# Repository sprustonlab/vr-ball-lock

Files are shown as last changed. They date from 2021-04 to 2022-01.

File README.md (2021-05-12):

# vr-ball-lock

## Notes
Theres a very bright LED on the PCA9685 board. I couldnt remove it by desodering but the board seems to work fine after I just broke the LED with a plier.
## testing the arduino uno control
You can add a simple jumper cable between digital pin 11 and 12. This will cycle between on/off every second.

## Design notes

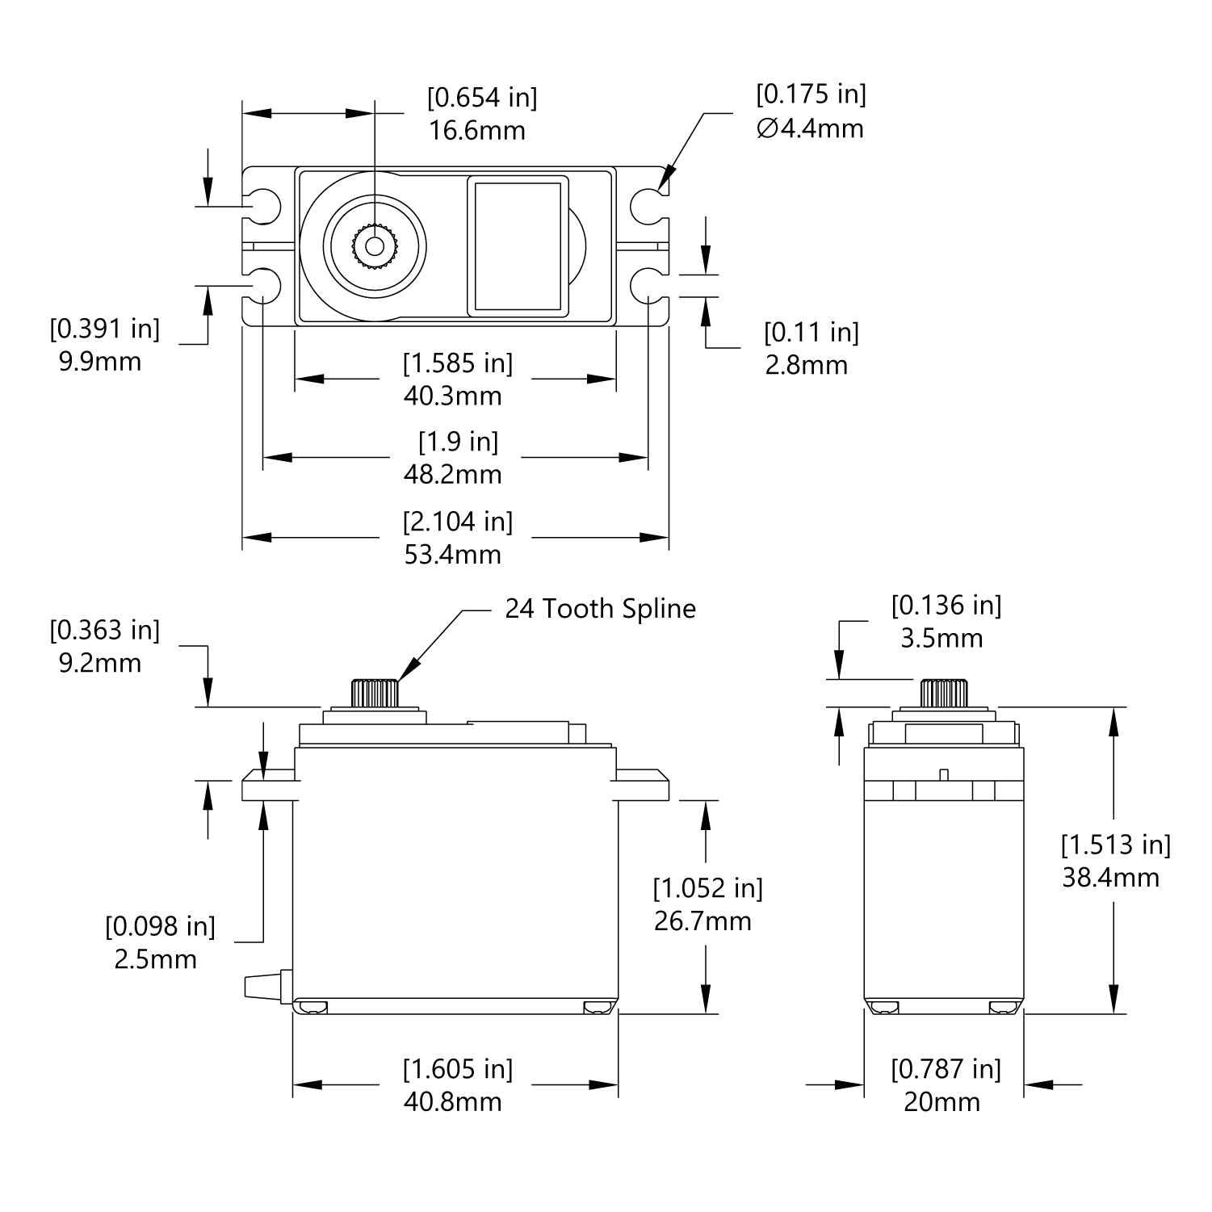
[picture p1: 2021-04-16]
Inventor Models/Parts/Hitec-HS-422-Schematic__34470.1591133086.png

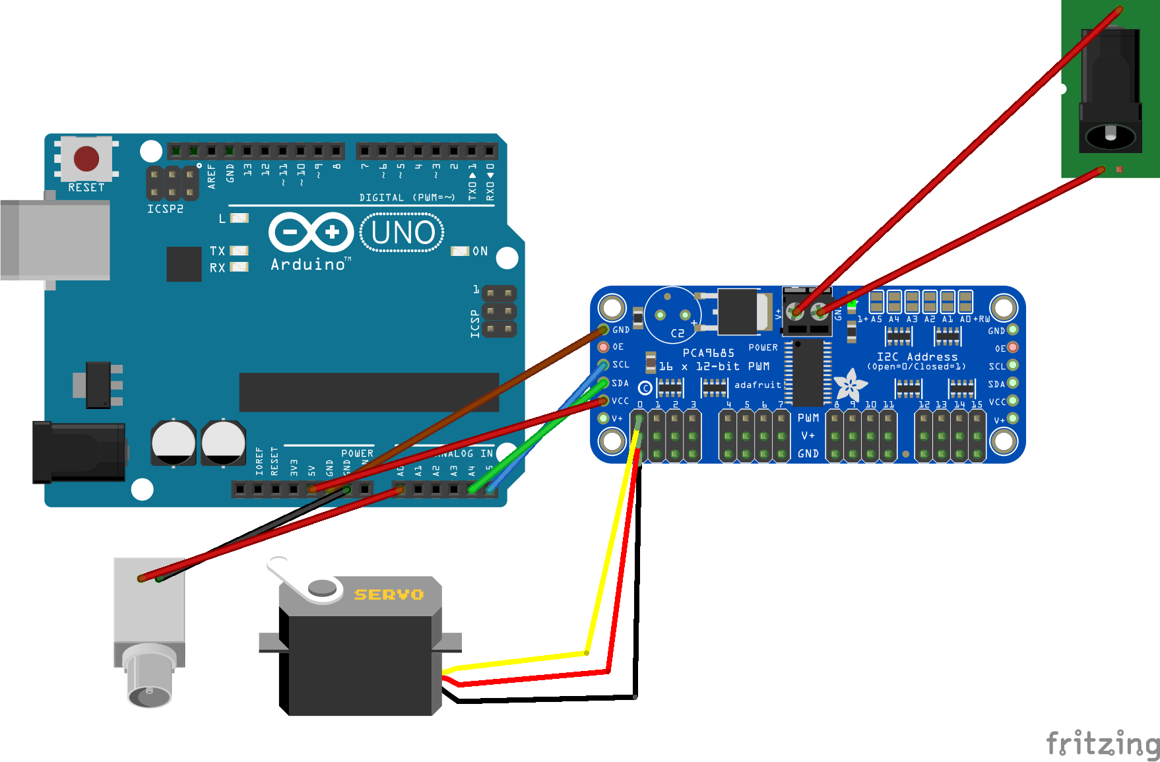
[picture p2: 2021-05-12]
electronics schematic/ball lock Schematic_bb.png

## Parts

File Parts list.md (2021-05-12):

# Main Components
* Servo: [HS-422 Deluxe Standard Servo | HITEC RCD USA](https://hitecrcd.com/products/servos/sport-servos/analog-sport-servos/hs-422/product)

* Servo Motor Driver PCA9685: [https://www.amazon.com/dp/B07Z8R2YB9](https://www.amazon.com/dp/B07Z8R2YB9) $13.99

* Arduino Uno: [https://www.amazon.com/dp/B008GRTSV6](https://www.amazon.com/dp/B008GRTSV6) $22.50

* Arduino Uno case: [https://www.amazon.com/dp/B01C8500L8](https://www.amazon.com/dp/B01C8500L8)$4.89

 * 5V 4A Power Supply Charger  DC 5.5mm x 2.1mm: [https://www.amazon.com/dp/B08VWVLBWF](https://www.amazon.com/dp/B08VWVLBWF) $11.99

# Conectors

* Female Red Black DC Power Pigtail Female Cable Lead Plug 10in 2.1x5.5mm [https://www.amazon.com/dp/B01N5JHFC0](https://www.amazon.com/dp/B01N5JHFC0) $8.59

* 1x Female Jack to AV 2 Screw Terminal Connector [https://www.amazon.com/dp/B07TT14RGF](https://www.amazon.com/dp/B07TT14RGF) $8.99 

# Cables
 * 1x 25 feet bnc cable [https://www.amazon.com/dp/B07R567S3J](https://www.amazon.com/dp/B07R567S3J) $31.99

 * 5.5mm x 2.1mm Extension Cord (5m), [https://www.amazon.com/dp/B08GZ8JP87](https://www.amazon.com/dp/B08GZ8JP87) $8.99

 * 900mm Servo Extension: [https://www.amazon.com/dp/B074SZXXGM](https://www.amazon.com/dp/B074SZXXGM) $10.90

 * Jumper wires: [https://www.amazon.com/dp/B07GD2BWPY](https://www.amazon.com/dp/B07GD2BWPY) $5.99

 # Power cable

## Cable fabrication (Steve)
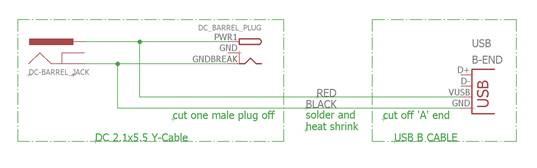
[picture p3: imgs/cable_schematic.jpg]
Schematic cable
 
 ## Off the shelf solution
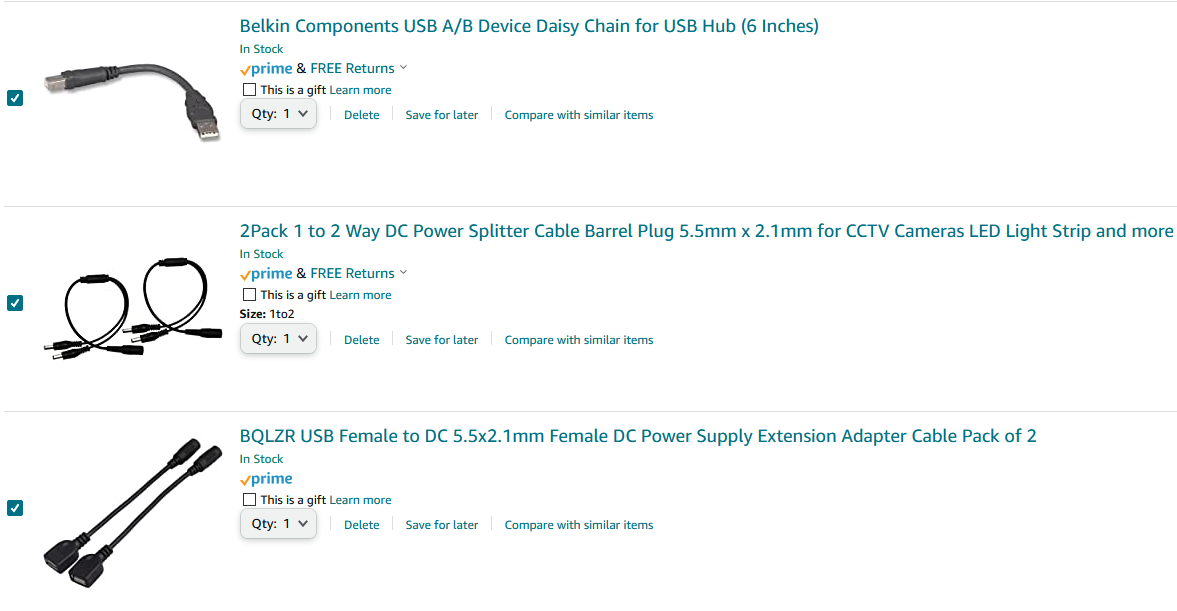
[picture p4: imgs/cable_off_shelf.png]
off the shelf cables


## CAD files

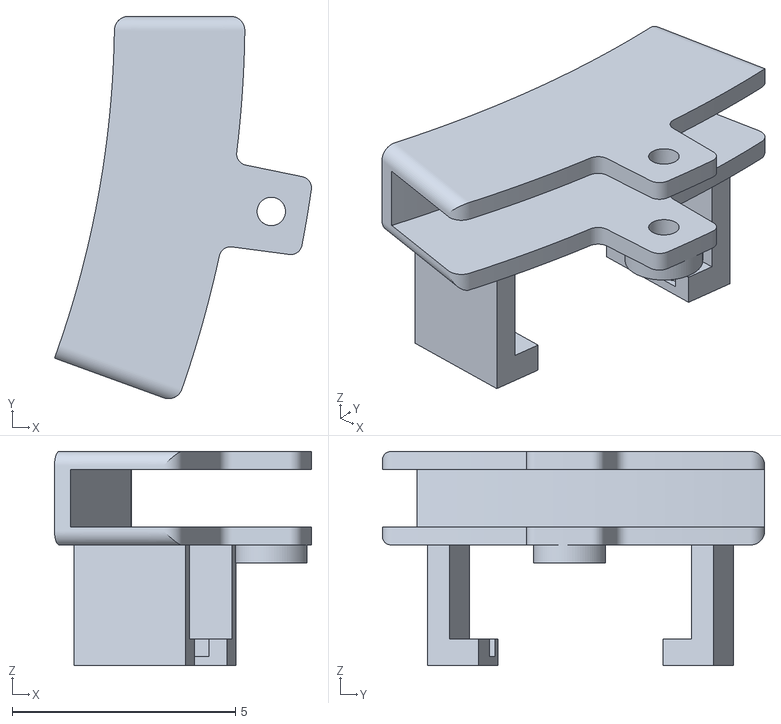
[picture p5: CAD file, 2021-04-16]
3d prints/Holder/Frame Holder.stl
5.75 x 8.56 x 4.80

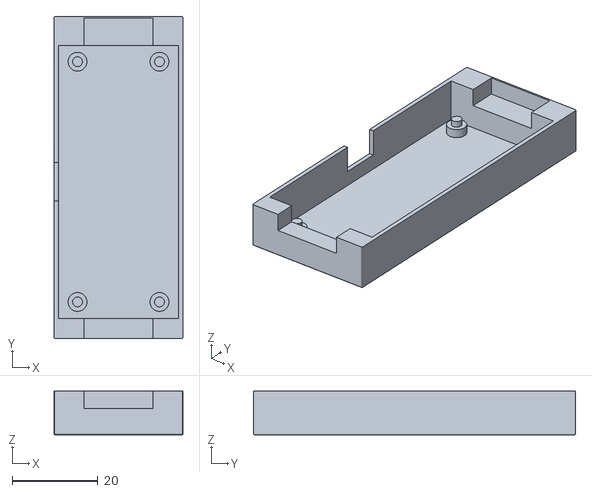
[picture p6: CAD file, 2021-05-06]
3d prints/PCA9685 case/Bottom_generic_v4.stl
30.0 x 75.0 x 10.2

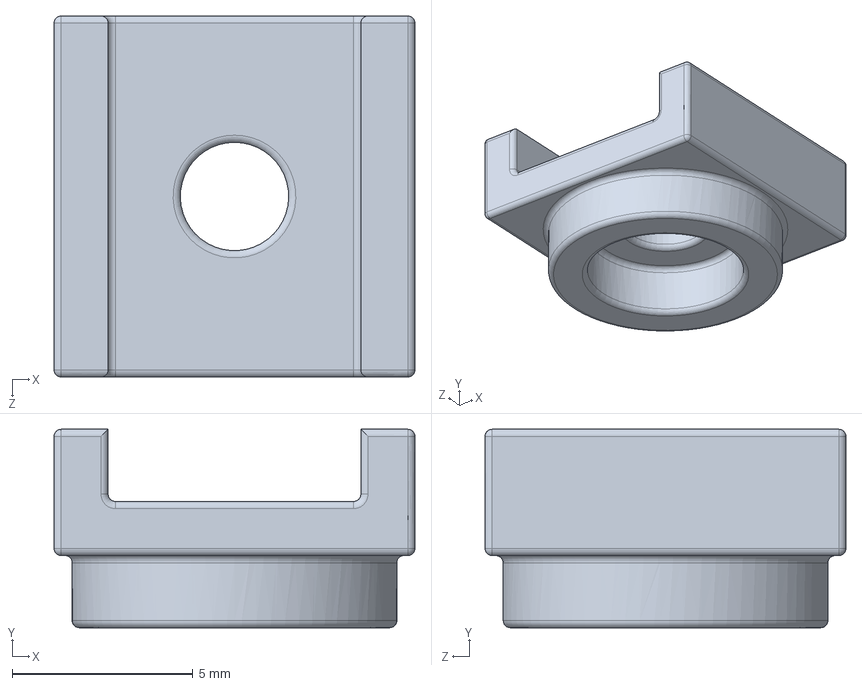
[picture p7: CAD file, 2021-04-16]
Inventor Models/Parts/base de riel.SLDPRT
10.0 x 5.50 x 10.0 mm

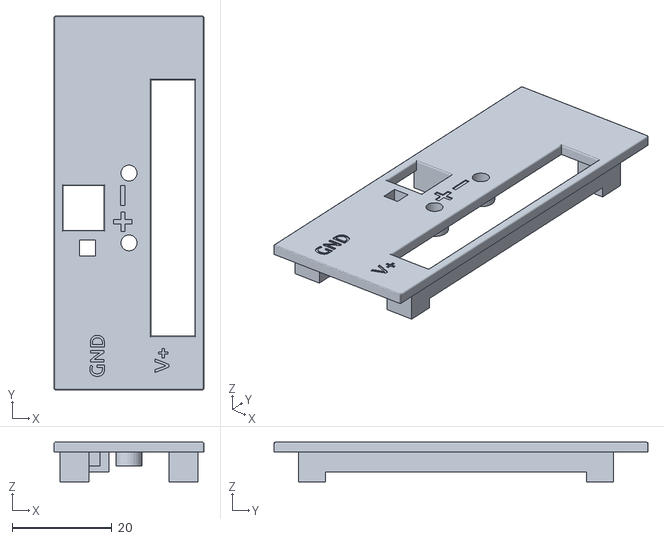
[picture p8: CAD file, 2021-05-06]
3d prints/PCA9685 case/Top_v4_ft_China.stl
30.0 x 75.0 x 8.00

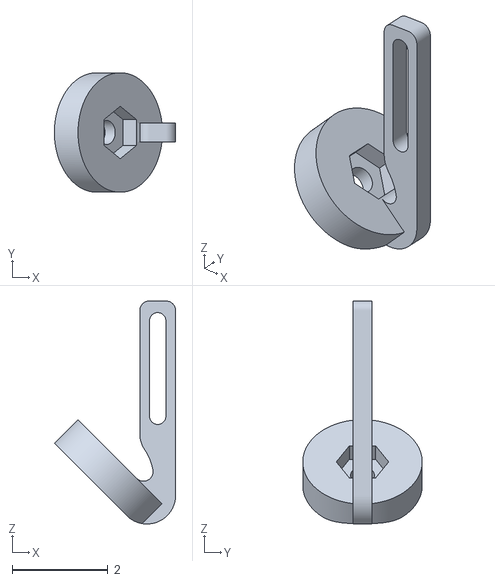
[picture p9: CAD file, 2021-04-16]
Inventor Models/Parts/arm.obj
2.54 x 2.50 x 4.67

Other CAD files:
Inventor Models/Parts/16 inch ball treadmill frame v2.ipt
Inventor Models/Parts/Frame Holder.ipt
Inventor Models/Parts/arm.ipt
Inventor Models/Parts/base de riel.ipt
Inventor Models/Parts/hs-422_sws.SLDPRT
Inventor Models/Parts/hs-422_sws.ipt
Inventor Models/Parts/servo connector.ipt
Inventor Models/Stop System Assembly.iam

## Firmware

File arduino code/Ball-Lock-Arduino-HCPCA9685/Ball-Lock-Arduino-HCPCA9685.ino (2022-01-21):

/*

  To use the PCA9685 module connect it to your Arduino as follows:

  PCA9685...........Uno/Nano
  GND...............GND
  OE................N/A
  SCL...............A5
  SDA...............A4
  VCC...............5V
*/


/* Include the HCPCA9685 library */
#include "HCPCA9685.h"

/* I2C slave address for the device/module. For the HCMODU0097 the default I2C address
   is 0x40 */
#define  I2CAdd 0x40

#define triggerPin A0   // Pin that receives TTL trigger signal.
#define ON_POSITION 117  // Angle of servos in ON state. (0-180)
#define OFF_POSITION 0   // Angle of servos in OFF state. (0-180)

unsigned long readBuffer; // Stores values of trigger pin.
bool motorState = false; // Stores current state of the motor so its only changed once per value change.

/* Create an instance of the library */
HCPCA9685 HCPCA9685(I2CAdd);

// Setup and Initialization Loop.
void setup()
{
  /* Initialise the library and set it to 'servo mode' */
  HCPCA9685.Init(SERVO_MODE);

  /* Wake the device up */
  HCPCA9685.Sleep(false);

  // Set mode of trigger pin.
  pinMode(triggerPin, INPUT);    // sets the trigger pin as input
  // Begin serial output.
  Serial.begin(9600);
  // Set Lock off.
  LockOff();
}

// LockOn. Turn on ball lock.
void LockOn()
{
  motorState = !motorState;
  MoveMotors(ON_POSITION);
  Serial.println("Lock On");
}

// LockOff. Turn off ball lock.
void LockOff()
{
  motorState = !motorState;
  MoveMotors(OFF_POSITION);
  Serial.println("Lock Off");
}

// MoveMotors. Moves all motors to requested angle. Called by LockOn/LockOff.
void MoveMotors(int angle) {
  for (int i = 0; i <= 15; i++) {
    HCPCA9685.Servo(i, map(angle,0,180,0,375) ); // maps angle to position (0-180 degrees to 0-375 (emprically determined)).
  }
}


// Main Loop.
void loop()
{
  // Read N samples of the trigger pin value. (avoids noise issues).
  for (int i = 0 ; i < 500 ; i++)
  {
    readBuffer = readBuffer+analogRead(triggerPin);
  }
  readBuffer = readBuffer/500; // average.
  Serial.println(readBuffer);

  // Check if state of trigger pin has changed.
  if (readBuffer>900 & !motorState) { LockOn(); }
  if (readBuffer<900 & motorState) { LockOff(); }
}

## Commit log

2021-04-16 Inventor files for model
    [16 inch ball treadmill frame v2.ipt, Frame Holder.ipt, Frame Holder.stl, Stop System Assembly.iam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]
2021-04-16 Update Stop System Assembly.iam
    [Stop System Assembly.iam]
2021-05-06 Added case and electronic connection schematics
    [Bottom_generic_v4.stl, Top_v4_ft_China.stl, ball lock schematic.fzz]
2021-05-12 Finishing up
    [ball lock schematic.fzz]
2021-05-12 Added notes on power cable
2021-06-11 Organized 3d prints
    [Bottom_generic_v4.stl, Frame Holder.stl, Top_v4_ft_China.stl]
